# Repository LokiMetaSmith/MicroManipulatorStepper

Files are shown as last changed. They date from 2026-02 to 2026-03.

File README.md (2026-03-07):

# Open Micro-Manipulator

This project contains an open source low-cost, easy-to-build motorized **XYZ Micro-Manipulator** motion control platform achieving submicron precision.
It's designed for applications such as optical alignment, probing electronic components, and microscopy.

Check out the YouTube video for more information about the device and how it is built:<br>
[An Open Source Motorized XYZ Micro-Manipulator - Affordable sub µm Motion Control](https://youtu.be/MgQbPdiuUTw)

<div style="display: flex; gap: 2%;">
  
  
</div>

Thanks to its parallel kinematic structure and miniature ball joints, it achieves good mechanical stiffness and a large range of motion.
The motors are off the shelf stepper motors driven by a 30 kHz closed loop controller and a very precise PWM signal.
A 'magnetic gearing' approach increases the resolution of the low-cost magnetic rotary encoders by a factor of 30 allowing for steps down to 50nm
(**Please mind the difference between resolution and accuracy**. The absolute accuracy is significantly worse.

The device can be controlled via simple G-Code commands over a USB serial interface and is thus easily integrated into other projects.
The firmware implements a complete motion planning stack with look-ahead for smooth and accurate path following capabilities.

## Getting Started

Below is a list of high level steps you can follow if you want to replicate the project. 
If you have questions or problems with the build or just want to discuss subjects related to the project, 
joint the projects community [Discord Server](https://discord.gg/maRvMVpa2Q).

1. Read this Document and watch the linked videos
2. Get the parts listed in [Bill of Materials](documentation/bom/bom.md)
3. Build the device and electronics
4. Change the hardware configuration according to your build [hw_config.h](firmware/MotionControllerRP/src/hw_config.h)
5. Upload firmware using VSCode with PlattformIO plugin
6. Calibrate axis

## ✨NEW: Hardware Version 4.0
A new version of the hardware has been released, fixing several issues with the previous design:

- Self collision during homing fixed.
- Connection of ball joint block with screws only was not well constrained and could rotated a bit.
- No reliable way to ensure consistent linkage rod length
- Unnecessary ball joint friction
- Accurate ball position heavily dependet on print quality and corner rounding
- Rubber bands could not be changed or removed once glued in.

A video about the improved ball joint and linkage manufactoring process can be found on YT: [Better Ball Joints for the Open Micro-Manipulator](https://www.youtube.com/watch?v=NM2KXvRGmpg)
Also the FreeCAD model was restructured and improved and now includes all pins and fasteners. It now provides a reference for all required mechanical parts. 

WARNING: BOM is not updated yet...

## Open Micro-Manipulator GUI
To make testing and using the Open-Micro Manipulator easy and convenient a python control program with a graphical user interface is provided here: [Open Micro-Manipulator GUI](https://github.com/0x23/OpenMicroManipulatorGUI).
It has simple controlls to move the device around, while also displaying a live camera feed (e.g. from a microscope camera). Additional features, include a simple g-code runner and realtime mouse control (e.g. for Biology applications).

<div style="display: flex;">
    Open Micro-Manipulator GUI
</div>

## 🐍 Python-API

The lightweight Python API handles all serial communication and provides convenient command execution and debug message printing.
The interface includes functions to home, move, and calibrate the device, as well as to query device information.
It is structured as a standard Python package for easy installation.

### Installation

You can install the package directly from the repository using pip:

```bash
pip install git+https://github.com/0x23/MicroManipulatorStepper.git#subdirectory=software/PythonAPI
```

Or, if you have cloned the repository locally:

```bash
pip install ./software/PythonAPI
```

## Usage Example
```python
from open_micro_manipulator import OpenMicroStageInterface
from open_micro_manipulator.exceptions import DeviceNotFoundError

# create interface and connect
# Use mock=True for simulation/digital twin
oms = OpenMicroStageInterface(show_communication=True, show_log_messages=True, mock=False)

try:
    oms.connect('/dev/ttyACM0')
except DeviceNotFoundError:
    print("Could not connect to device")

# run this once to calibrate joints
# for i in range(3): oms.calibrate_joint(i, save_result=True)

# home device
oms.home()

# move to several x,y,z positions [mm]
oms.move_to(0.0, 0.0, 0.0, f=10)
oms.move_to(3.1, 4.1, 5.9, f=26)
oms.move_to(0.0001, 0.0, 0.0, f=10)

# wait for moves to finish
oms.wait_for_stop()
```

## API Functions (most relevant functions only)
```python
connect(port, baud_rate=921600)
disconnect()
set_workspace_transform(transform)
get_workspace_transform()
home(axis_list=None)
calibrate_joint(joint_index, save_result)
move_to(x, y, z, f, move_immediately, blocking, timeout)
set_pose(x, y, z)
dwell(time_s, blocking, timeout)
enable_motors(enable)
wait_for_stop(polling_interval_ms, disable_callbacks)
set_max_acceleration(linear_accel, angular_accel)
set_servo_parameter(pos_kp, pos_ki, vel_kp, vel_ki, vel_filter_tc)
```

## ✨ Firmware v1.0.1

This update improves calibration, homing, logging, and adds several new G-Code commands.

### Improvements
- **Homing**: parallel homing support, higher repeatability, more accurate geometric reference  
- **Joint calibration**: refined procedure, persistent flash storage (no recalibration after reboot)  
- **Logging**: clearer and more detailed output  

### New G-Code Commands
- `G28` — Home joints (supports homing multiple axis simultanously for faster startup)
- `G24` — Set pose command (directly sets servo targets, bypassing motion controller)  
- `M17/M18` — Enable/Disable motors (with pose recovery from encoders on enable)  
- `M51` — Read encoder values  
- `M55` — Set servo loop parameters 
- `M56` — Joint calibration (with save-to-flash option)  
- `M57` — Read various information about the device state  
- `M58` — Read firmware version

## ⚙ CAD-Files

All CAD models are made in **FreeCAD** to allow everyone to view and modify the design without subscribing or paying for a proprietary CAD solution.
Note that most components are already designed with the goal to make them easily machinable on a 3-Axis CNC-Mill.
You can also 3D-Print the parts but have to live with thermal drift (carbon filled filaments can reduce this problem).

<div style="display: flex;">
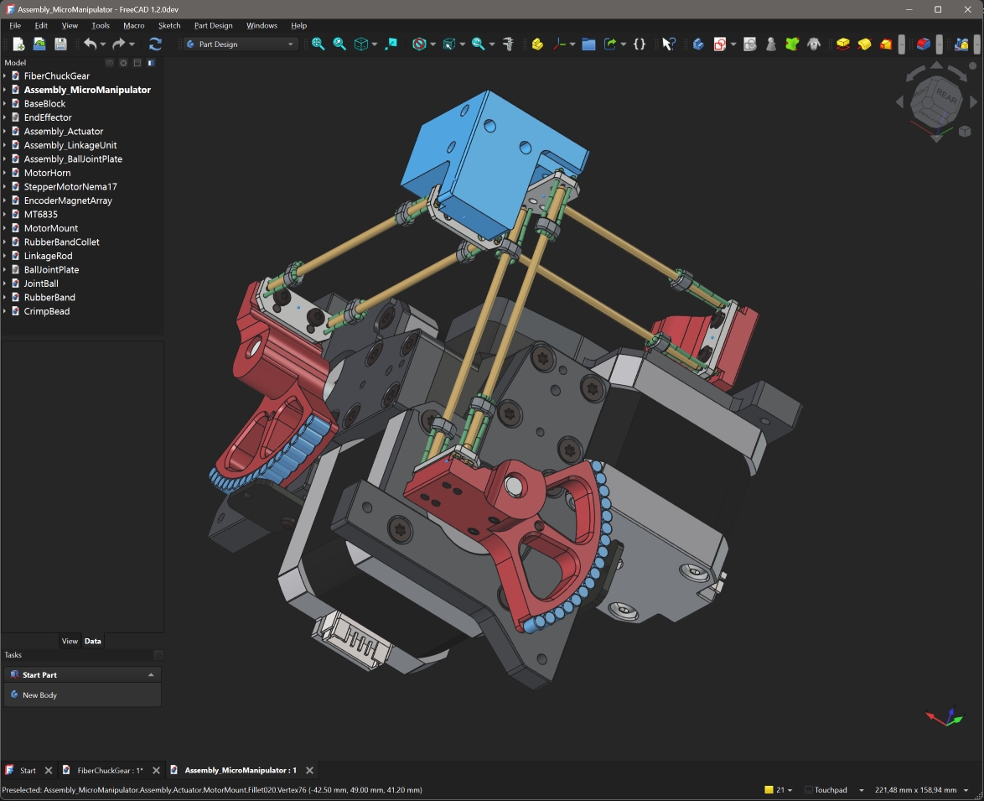
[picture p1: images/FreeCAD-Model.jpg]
FreeCAD Model
    
</div>

<br>

The CAD files can be found here: [CAD Models](construction).
Please note that FreeCAD version **1.2.0dev** was used, and the files might not work with older versions.

STL files for printing can be found here: [STL Files](construction/STL_3D_Printing/)

## ⚙ Testing & Simulation

This project now includes Python scripts for unit testing CAD models, verifying kinematics, and setting up FEA simulations.
See [tests/freecad_scripts/README.md](tests/freecad_scripts/README.md) for details.

To run tests (requires FreeCAD):
```bash
freecadcmd tests/freecad_scripts/run_all_tests.py
```

## ⚙ Kinematic Model

The kinematic model is defined here: [kinematic_model_delta3d.cpp](firmware/MotionControllerRP/src/kinemtaic_models/kinematic_model_delta3d.cpp).
Please check the dimensions of your build against the values set in the constructor. In particular, make sure the arm length matches.

## ⚙ Electronics

IMPORTANT: If you fabricated PCB version v1.2 (see version label on the board) you need to drill out a misplaced via on diode D1 that shorts 5V rail to ground (See [repair image](electronics/pcb_v1.2_fix.jpg) ). The problem was fixed in v1.3.

The electronics are designed in **KiCAD** and only commonly available modules (motor drivers and MCU boards) are used and connected by a simple PCB. No SMD soldering is required to populate the board to make the build extra accessible.
For usual winding resistance of your motors, the device should be powered by $${\color{lightgreen} 5V-6V }$$ (2A) to keep current and heating to a reasonable level.

<div style="display: flex; gap: 5%;">
  
  
</div>

The repository now also contains the fabrication files that can be directly uploaded to the PCB manufacturer.

## ⚙ Firmware

The firmware is written in C++ and takes some inspiration from the 'SimpleFOC' project. It aims to be streamlined and readable without any extra fuss, focusing on the hardware used in this project.
It implements path planning with look-ahead and, unlike many other motion controller projects, supports true 6DOF-Pose interpolation and planning, making it ready for driving hexapod motion platforms; that may or may not be the next step for this project.

You may find configuration for pin numbers, motor type, and other parameters in [hw_config.h](firmware/MotionControllerRP/src/hw_config.h). Please check them before uploading the firmware.

<div style="display: flex; gap: 2%;">
  
  
</div>

### Building and Flashing the Firmware

For building and flashing the firmware, Visual Studio Code (available for free on Windows and Linux) is recommended.
Install the PlatformIO add-on and open the firmware folder. You can now build and flash the firmware like any other PlatformIO project.

## ⚙ G-Code Interface

The firmware supports only a small subset of G-Code commands listed below.  
Each command is acknowledged with either an **`ok`** or **`error`** response.  

If a command provides additional information (e.g., the *get position* command), that information is returned **before** the `ok` message.  
The client must wait for an acknowledgment from the previous command before sending the next one—otherwise, behavior is undefined.
| Command           | Description                                                                 |
|-------------------|-----------------------------------------------------------------------------|
| `G0 X Y Z F`   | Move the end-effector in a straight line to the specified position. <br>• `X`, `Y`, `Z`: target positions <br>• `F`: feed rate |
| `G1 X Y Z F`   | Same as `G0`.                                                              |
| `G4 S/P`       | Dwell/pause for a specified time. <br>• `S`: seconds <br>• `P`: milliseconds |
| `G24 X Y Z A B C` | Directly set current pose for servo loops with optional rotation vector* `A`, `B`, `C`. |
| `G28 A-F`      | Home one or more joints. <br>• Optional joint selection `A`–`F`.           |
| `M17`          | Enable motors and read current pose as the start pose.                     |
| `M18`          | Disable motors.                                                            |
| `M50`          | Get current internal pose. (Encoders are not read here)                                   |
| `M51`          | Get current encoder angles (in degrees) and raw encoder values.              |
| `M52`          | Get the number of items in the planner queue.                               |
| `M53`          | Check if all planned moves are finished (`1` = finished, `0` = not finished). |
| `M55 A B C D F` | Set servo loop parameters. <br>• `A`, `B`: position PI controller gains (P and I) <br>• `C`, `D`: velocity PI controller gains (P and I) <br>• `F`: velocity filter time constant |
| `M56 J S`      | Calibrate a joint. <br>• `J`: joint index <br>• `S`: save calibration result |
| `M57`          | Get device and servo loop info: homing/calibration state, angles, loop frequencies, and file list. |
| `M58`          | Get firmware version.                                                      |
| `M204 L A`     | Set linear and angular acceleration. <br>• `L`: linear acceleration <br>• `A`: angular acceleration |

*Note: The communication protocol uses 3D vectors for rotations. The direction represents the rotation axis and the length of the vector represents the angle of rotation around the axis.

## ❤️ Support

If you'd like to support this project, consider the following:

- **Contribute to the build guide** – Help improve or expand the build instructions by submitting pull requests or opening issues with suggestions.
- **Characterize typical radial stepper motor shaft error motion** – Measure radial error motion of the shaft of multiple Nema-17 stepper motors (see Cylos Garage for more information about the subject: https://www.youtube.com/watch?v=gt2gK-oxy5s).
- **Give feedback on the build experience** – Let us know what worked, what didn’t, and how the process could be smoother for others.
- **Support the project on Ko-fi** – If you find this project valuable, you can support it financially via [Ko-fi](https://ko-fi.com/diffractionlimited) ☕.

## Youtube Video
Watch the video (https://youtu.be/MgQbPdiuUTw)

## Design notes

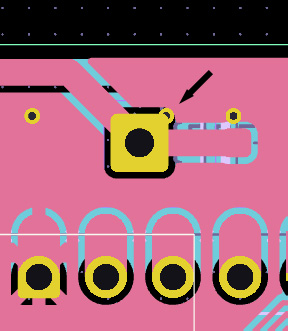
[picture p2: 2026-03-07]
electronics/control_board/pcb_v1.2_fix.jpg

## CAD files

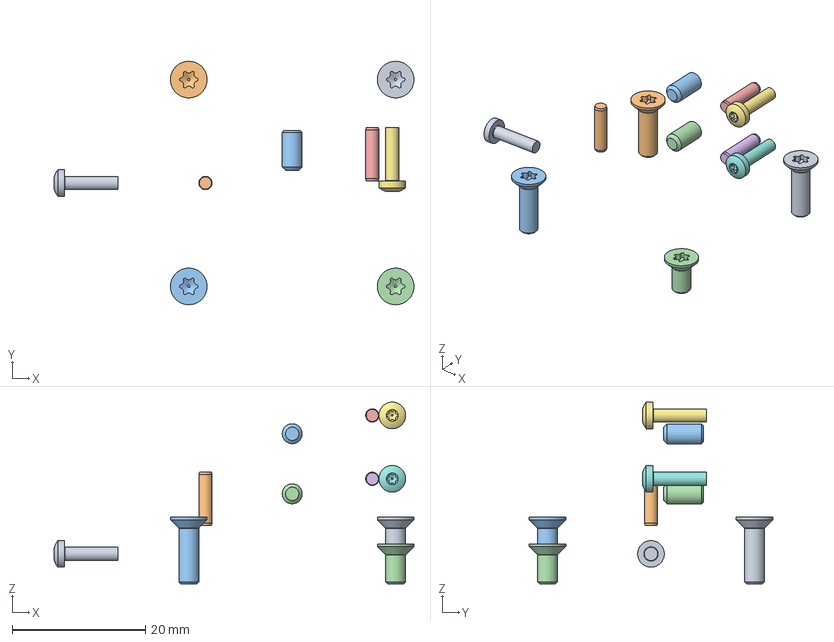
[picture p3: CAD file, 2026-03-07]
construction/micro_manipulator/Assembly_Actuator.FCStd
53.9 x 36.5 x 27.2 mm
M3x10-Screw x 2
M3x10-Screw008 x 2
M3x10-Screw009 x 2
M3x6-Screw x 2
2 mmx8-Pin x 2
2 mmx8-Pin012 x 2
M2x8-Screw x 2
M2x8-Screw009 x 2
M2x8-Screw004 x 2
2 mmx8-Pin011 x 2
M3x6-Screw003 x 2
M3x6-Screw004 x 2

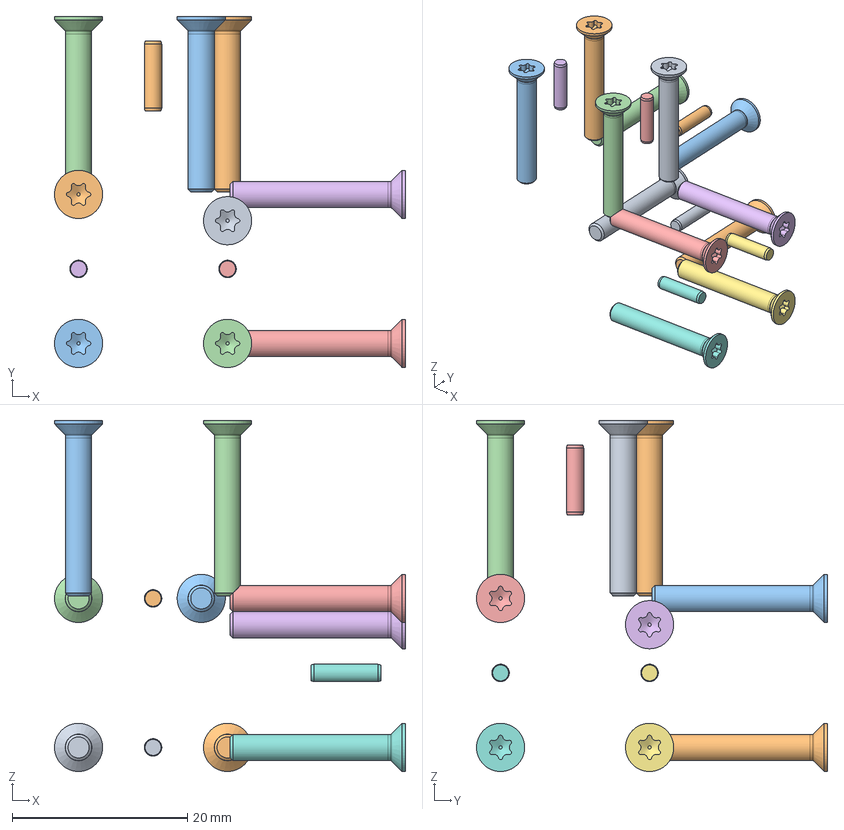
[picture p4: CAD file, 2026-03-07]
construction/micro_manipulator/Assembly_MicroManipulator.FCStd
40.0 x 40.0 x 40.0 mm
M3x20-Screw x 2
M3x20-Screw281 x 2
M3x20-Screw282 x 2
M3x20-Screw283 x 2
M3x20-Screw277 x 2
M3x20-Screw278 x 2
M3x20-Screw279 x 2
M3x20-Screw280 x 2
M3x20-Screw262 x 2
M3x20-Screw263 x 2
M3x20-Screw264 x 2
M3x20-Screw265 x 2
2 mmx8-Pin027 x 2
2 mmx8-Pin028 x 2
2 mmx8-Pin029 x 2
2 mmx8-Pin030 x 2
2 mmx8-Pin031 x 2
2 mmx8-Pin032 x 2

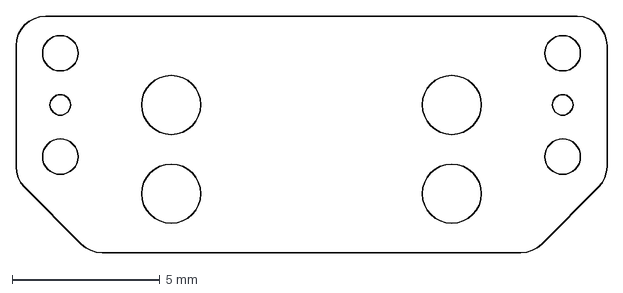
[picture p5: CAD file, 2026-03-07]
construction/micro_manipulator/balljoint_plate_pcb/BallJointPlate-Contour.dxf
20.0 x 8.00 mm

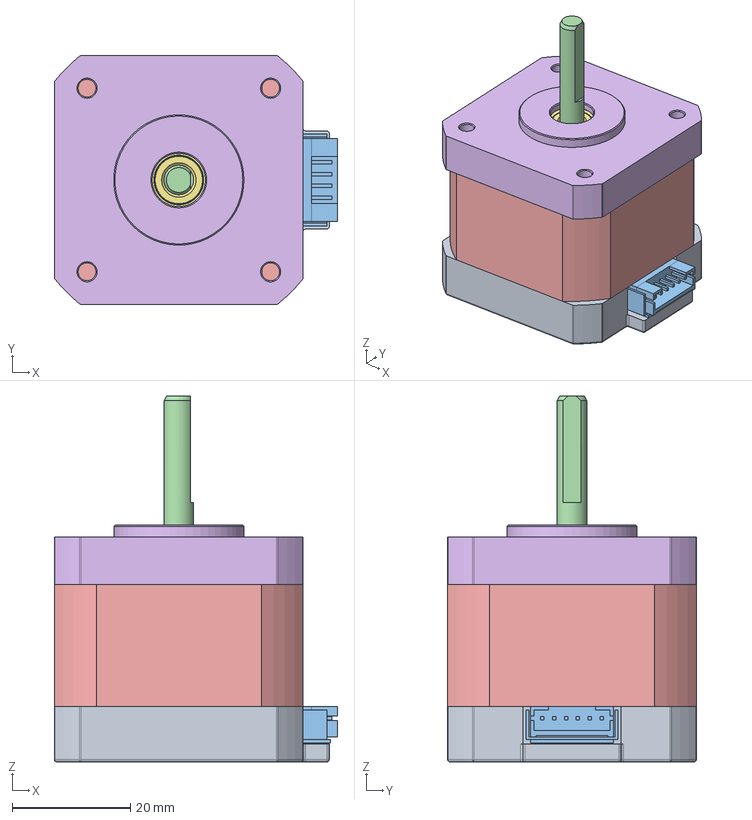
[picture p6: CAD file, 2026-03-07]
construction/micro_manipulator/StepperMotorNema17.FCStd
47.8 x 42.0 x 61.8 mm
rear end cap
rear bearing
connector
shaft
stator
front end cap
front bearing
M3x10-Screw
M3x10-Screw004
M3x10-Screw005
M3x10-Screw006

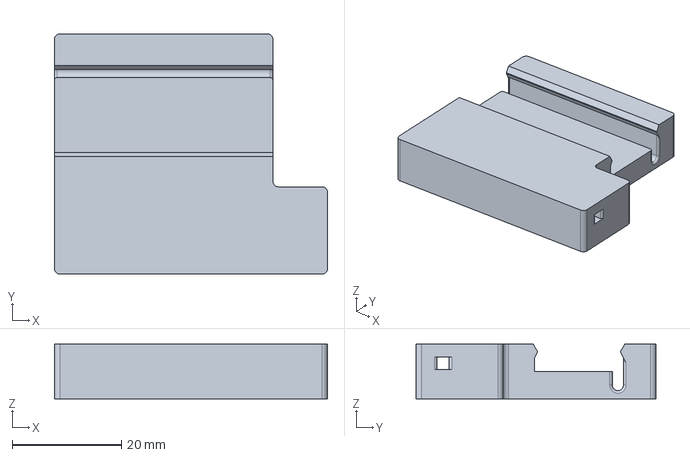
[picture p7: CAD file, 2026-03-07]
construction/tools/rod_embossing_tools/rod_lenth_setting_press/rod_guide.FCStd
50.0 x 44.0 x 10.0 mm

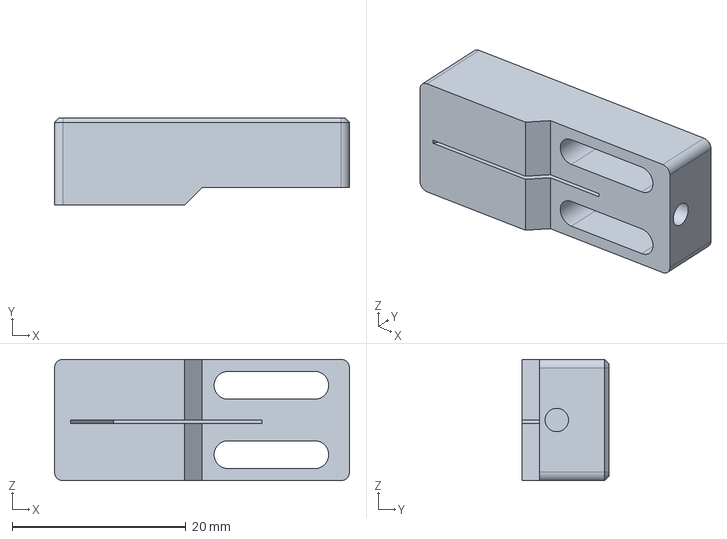
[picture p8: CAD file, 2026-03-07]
construction/tools/rod_embossing_tools/rod_sharper/BladeCarrier.FCStd
34.0 x 10.0 x 14.0 mm

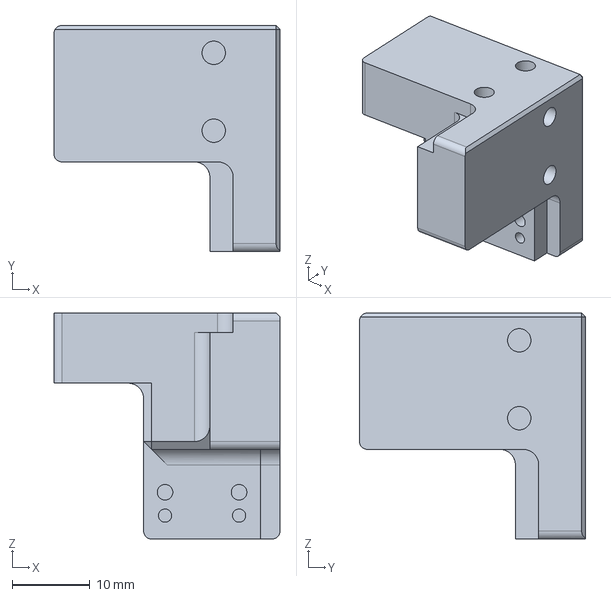
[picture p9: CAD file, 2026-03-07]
construction/micro_manipulator/EndEffector.FCStd
29.0 x 29.0 x 29.0 mm

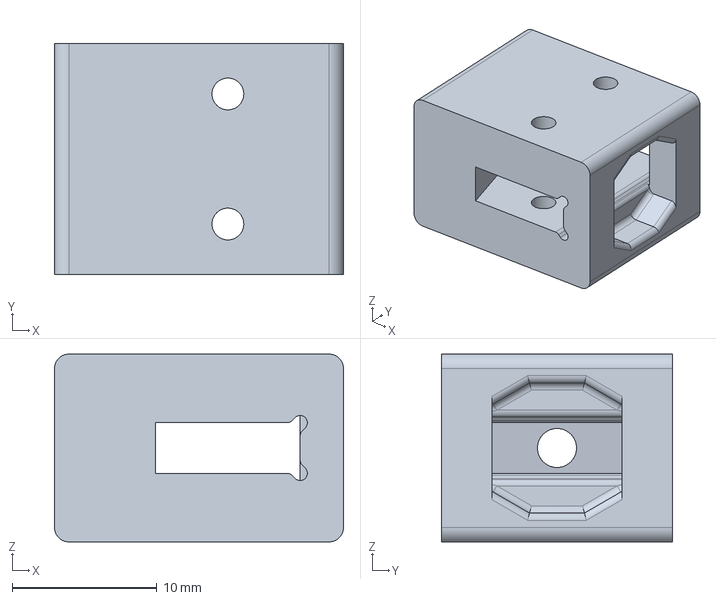
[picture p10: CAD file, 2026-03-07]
construction/tools/rod_embossing_tools/rod_lenth_setting_press/caliper_clamp.FCStd
20.0 x 16.0 x 13.0 mm

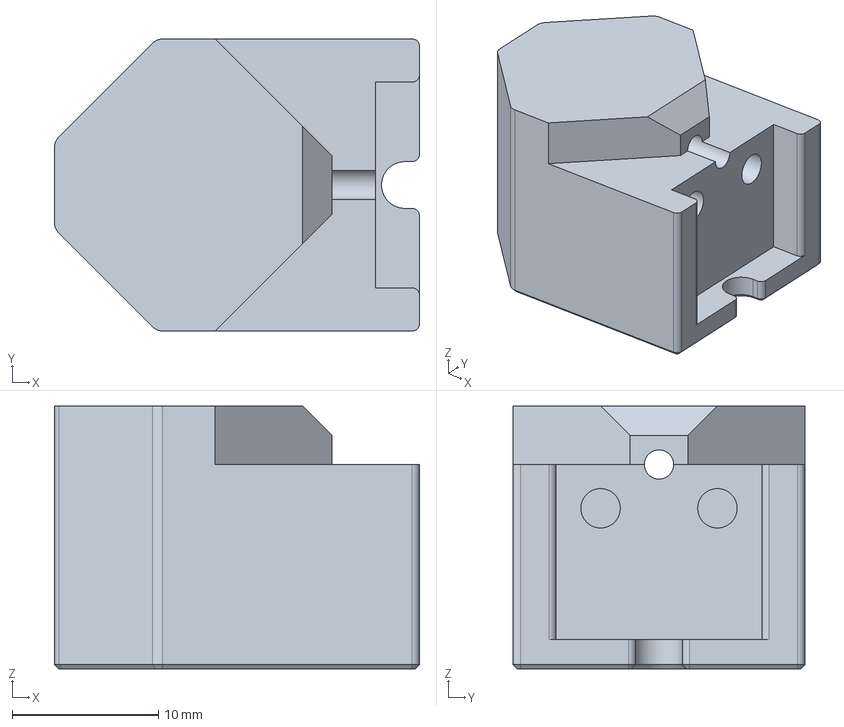
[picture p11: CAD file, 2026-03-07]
construction/tools/rod_embossing_tools/rod_sharper/RodGuide.FCStd
25.0 x 20.0 x 18.0 mm

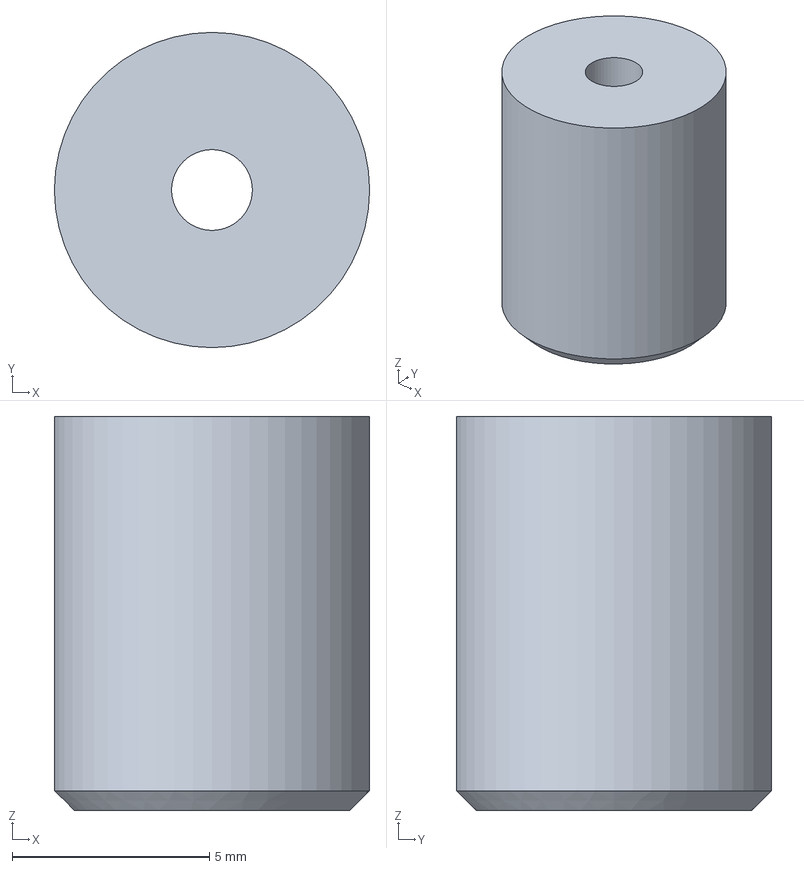
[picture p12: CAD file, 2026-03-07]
construction/tools/rod_embossing_tools/rod_lenth_setting_press/rod_collet.FCStd
8.00 x 8.00 x 10.0 mm

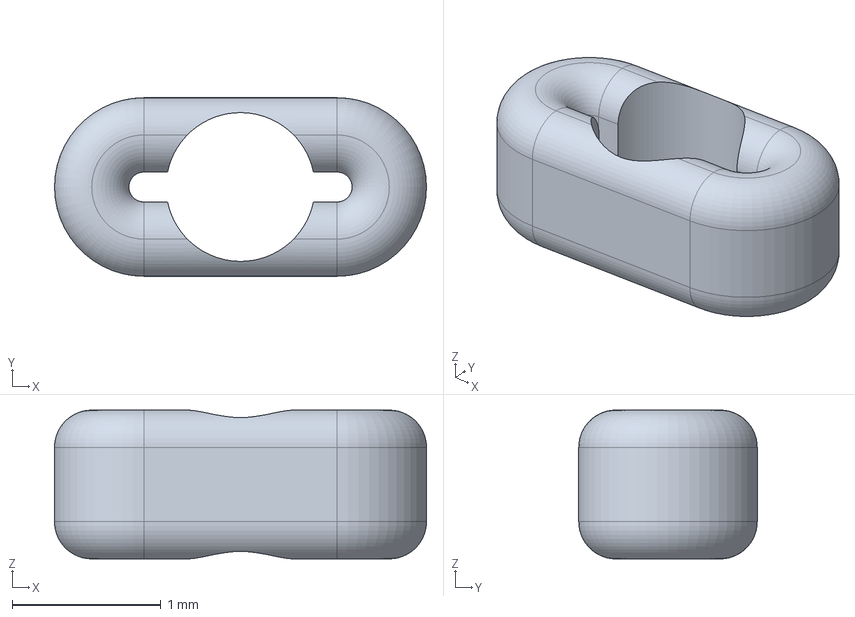
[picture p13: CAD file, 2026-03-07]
construction/micro_manipulator/CrimpBead.FCStd
2.50 x 1.20 x 1.00 mm

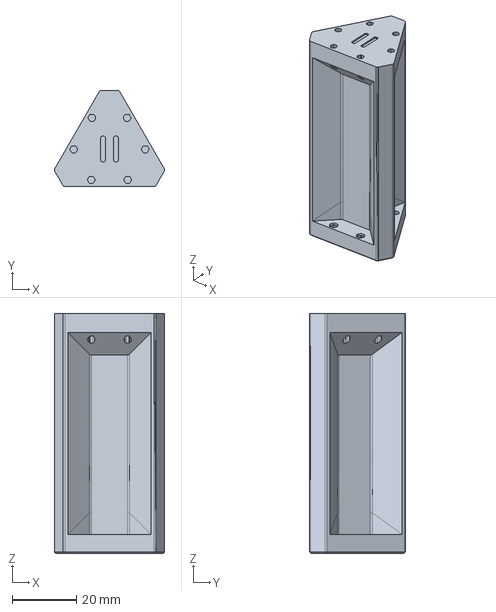
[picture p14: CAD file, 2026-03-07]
construction/tools/rod_embossing_tools/rod_lenth_setting_press/RodGrindingJig_B.FCStd
34.5 x 30.1 x 75.0 mm

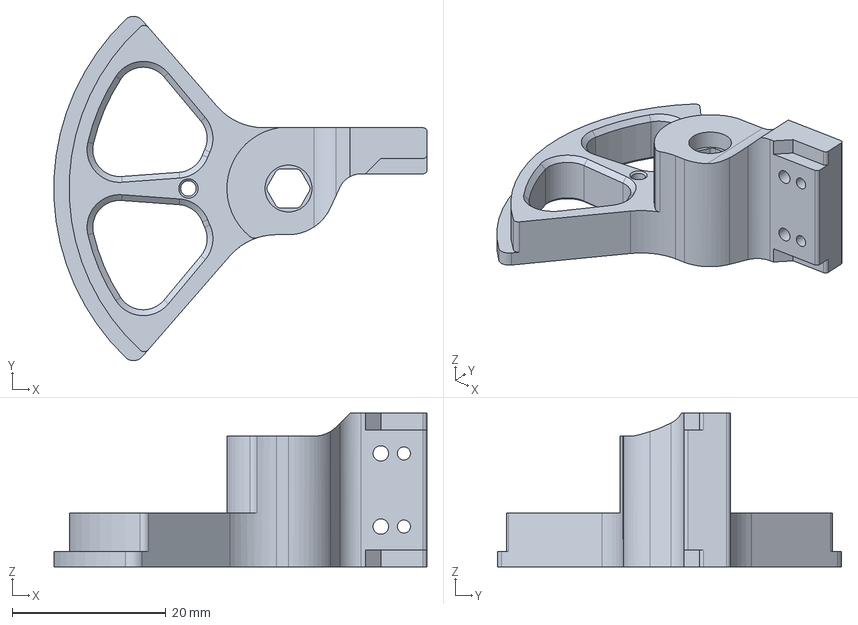
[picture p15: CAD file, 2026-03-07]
construction/micro_manipulator/MotorHorn.FCStd
48.5 x 44.7 x 20.0 mm

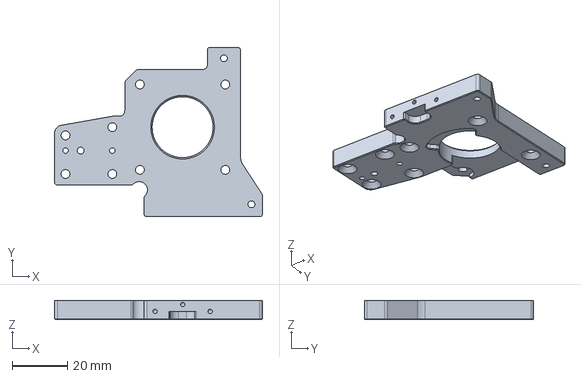
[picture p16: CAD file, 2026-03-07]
construction/micro_manipulator/MotorMount.FCStd
75.5 x 61.5 x 7.00 mm

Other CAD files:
construction/micro_manipulator/Assembly_EndEffector.FCStd
construction/micro_manipulator/Assembly_BallJointPlate.FCStd
construction/micro_manipulator/Assembly_LinkageUnit.FCStd
construction/tools/rod_embossing_tools/rod_lenth_setting_press/RodGrindingJig_A.FCStd
construction/micro_manipulator/BallJointPlate.FCStd
construction/micro_manipulator/BaseBlock.FCStd
construction/micro_manipulator/EncoderMagnet.FCStd
construction/micro_manipulator/EncoderMagnetArray.FCStd
construction/micro_manipulator/JointBall.FCStd
construction/micro_manipulator/LinkageRod.FCStd
construction/micro_manipulator/MT6835.FCStd
construction/micro_manipulator/RubberBand.FCStd
construction/micro_manipulator/RubberBandCollet.FCStd

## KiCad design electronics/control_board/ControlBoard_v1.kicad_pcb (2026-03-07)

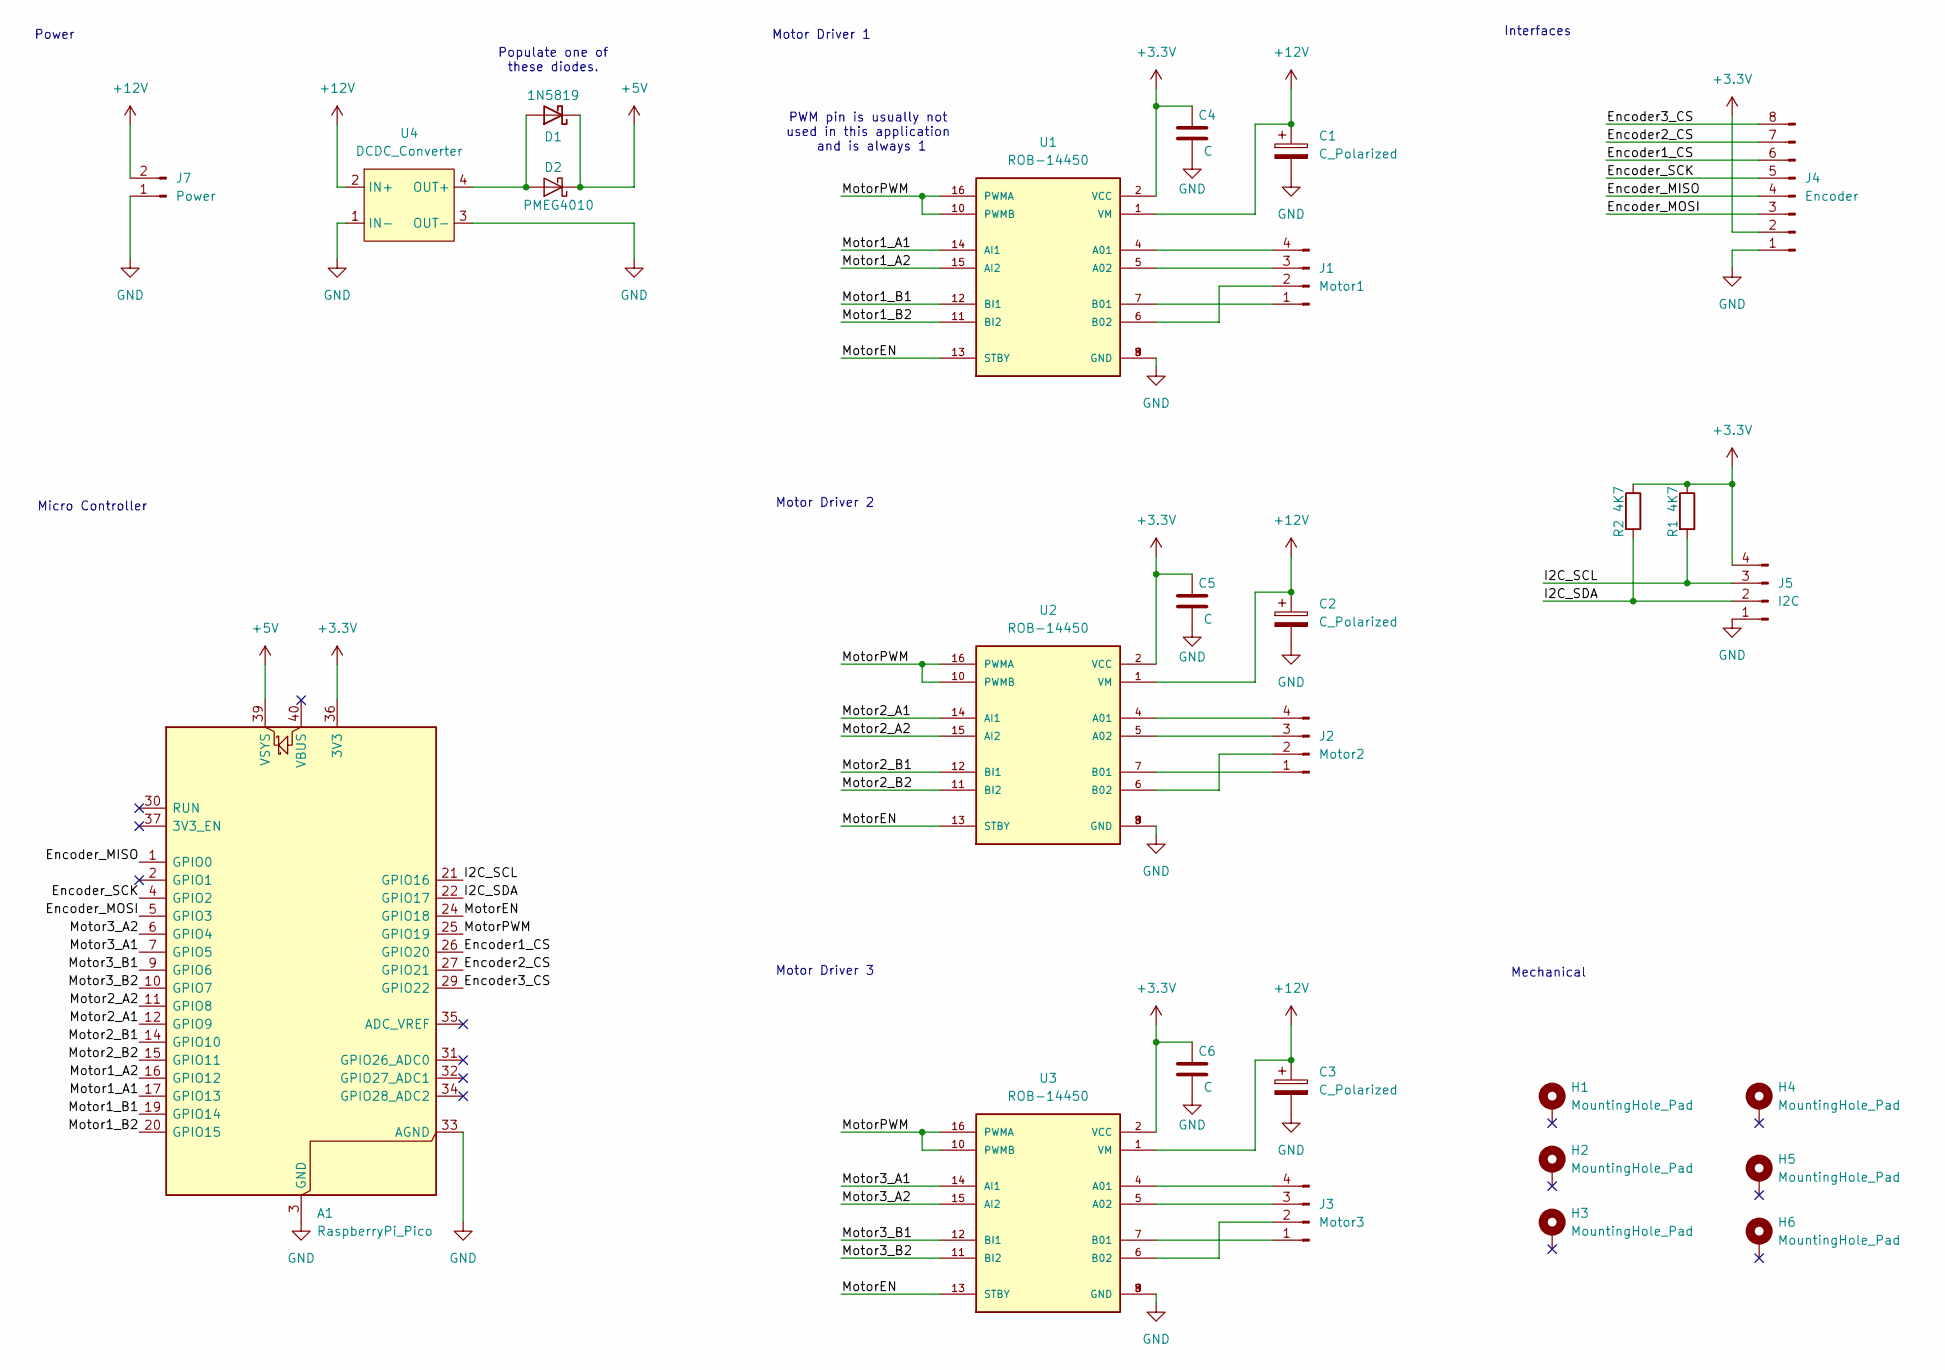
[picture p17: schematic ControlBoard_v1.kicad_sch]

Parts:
A1: RaspberryPi_Pico; RaspberryPi_Pico_Common_Unspecified
C1, C2, C3: C_Polarized; CP_Radial_D8.0mm_P3.50mm
C4, C5, C6: C; C_0603_1608Metric_Pad1.08x0.95mm_HandSolder
D1: 1N5819; D_DO-41_SOD81_P10.16mm_Horizontal
D2: PMEG4010; D_SOD-123F
H1, H2, H3, H4, H5, H6: MountingHole_Pad; MountingHole_2.7mm_M2.5_Pad_Via
J1: Motor1; PinHeader_1x04_P2.54mm_Vertical
J2: Motor2; PinHeader_1x04_P2.54mm_Vertical
J3: Motor3; PinHeader_1x04_P2.54mm_Vertical
J4: Encoder; JST_PH_B8B-PH-K_1x08_P2.00mm_Vertical
J5: I2C; JST_PH_B4B-PH-K_1x04_P2.00mm_Vertical
J7: Power; AMASS_XT60-M_1x02_P7.20mm_Vertical
R1, R2: 4K7; R_0603_1608Metric_Pad0.98x0.95mm_HandSolder
U1, U2, U3: ROB-14450; MODULE_ROB-14450; PARTREV 11-13-17
U4: DCDC_Converter; DCDC_17mmx12mm

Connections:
+3.3V: A1.36 (3V3), C4.1, C5.1, C6.1, J4.2, J5.4, R1.1, R2.1, U1.2 (VCC), U2.2 (VCC), U3.2 (VCC)
+5V: A1.39 (VSYS), D1.1 (K), D2.1 (K)
+12V: C1.1, C2.1, C3.1, J7.2, U1.1 (VM), U2.1 (VM), U3.1 (VM), U4.2 (IN+)
/Encoder1_CS: A1.26 (GPIO20), J4.6
/Encoder2_CS: A1.27 (GPIO21), J4.7
/Encoder3_CS: A1.29 (GPIO22), J4.8
/Encoder_MISO: A1.1 (GPIO0), J4.4
/Encoder_MOSI: A1.5 (GPIO3), J4.3
/Encoder_SCK: A1.4 (GPIO2), J4.5
/I2C_SCL: A1.21 (GPIO16), J5.3, R1.2
/I2C_SDA: A1.22 (GPIO17), J5.2, R2.2
/Motor1_A1: A1.17 (GPIO13), U1.14 (AI1)
/Motor1_A2: A1.16 (GPIO12), U1.15 (AI2)
/Motor1_B1: A1.19 (GPIO14), U1.12 (BI1)
/Motor1_B2: A1.20 (GPIO15), U1.11 (BI2)
/Motor2_A1: A1.12 (GPIO9), U2.14 (AI1)
/Motor2_A2: A1.11 (GPIO8), U2.15 (AI2)
/Motor2_B1: A1.14 (GPIO10), U2.12 (BI1)
/Motor2_B2: A1.15 (GPIO11), U2.11 (BI2)
/Motor3_A1: A1.7 (GPIO5), U3.14 (AI1)
/Motor3_A2: A1.6 (GPIO4), U3.15 (AI2)
/Motor3_B1: A1.9 (GPIO6), U3.12 (BI1)
/Motor3_B2: A1.10 (GPIO7), U3.11 (BI2)
/MotorEN: A1.24 (GPIO18), U1.13 (STBY), U2.13 (STBY), U3.13 (STBY)
/MotorPWM: A1.25 (GPIO19), U1.10 (PWMB), U1.16 (PWMA), U2.10 (PWMB), U2.16 (PWMA), U3.10 (PWMB), U3.16 (PWMA)
GND: A1.3 (GND), A1.8 (GND), A1.13 (GND), A1.18 (GND), A1.23 (GND), A1.28 (GND), A1.33 (AGND), A1.38 (GND), C1.2, C2.2, C3.2, C4.2, C5.2, C6.2, J4.1, J5.1, J7.1, U1.3 (GND), U1.8 (GND), U1.9 (GND), U2.3 (GND), U2.8 (GND), U2.9 (GND), U3.3 (GND), U3.8 (GND), U3.9 (GND), U4.1 (IN-), U4.3 (OUT-)
unnamed: D1.2 (A), D2.2 (A), U4.4 (OUT+)
unnamed: J1.1, U1.7 (B01)
unnamed: J1.2, U1.6 (B02)
unnamed: J1.3, U1.5 (A02)
unnamed: J1.4, U1.4 (A01)
unnamed: J2.1, U2.7 (B01)
unnamed: J2.2, U2.6 (B02)
unnamed: J2.3, U2.5 (A02)
unnamed: J2.4, U2.4 (A01)
unnamed: J3.1, U3.7 (B01)
unnamed: J3.2, U3.6 (B02)
unnamed: J3.3, U3.5 (A02)
unnamed: J3.4, U3.4 (A01)

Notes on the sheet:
PWM pin is usually not used in this application and is always 1
Motor Driver 2
Power
Interfaces
Motor Driver 1
Motor Driver 3
Mechanical
Populate one of these diodes.
Micro Controller

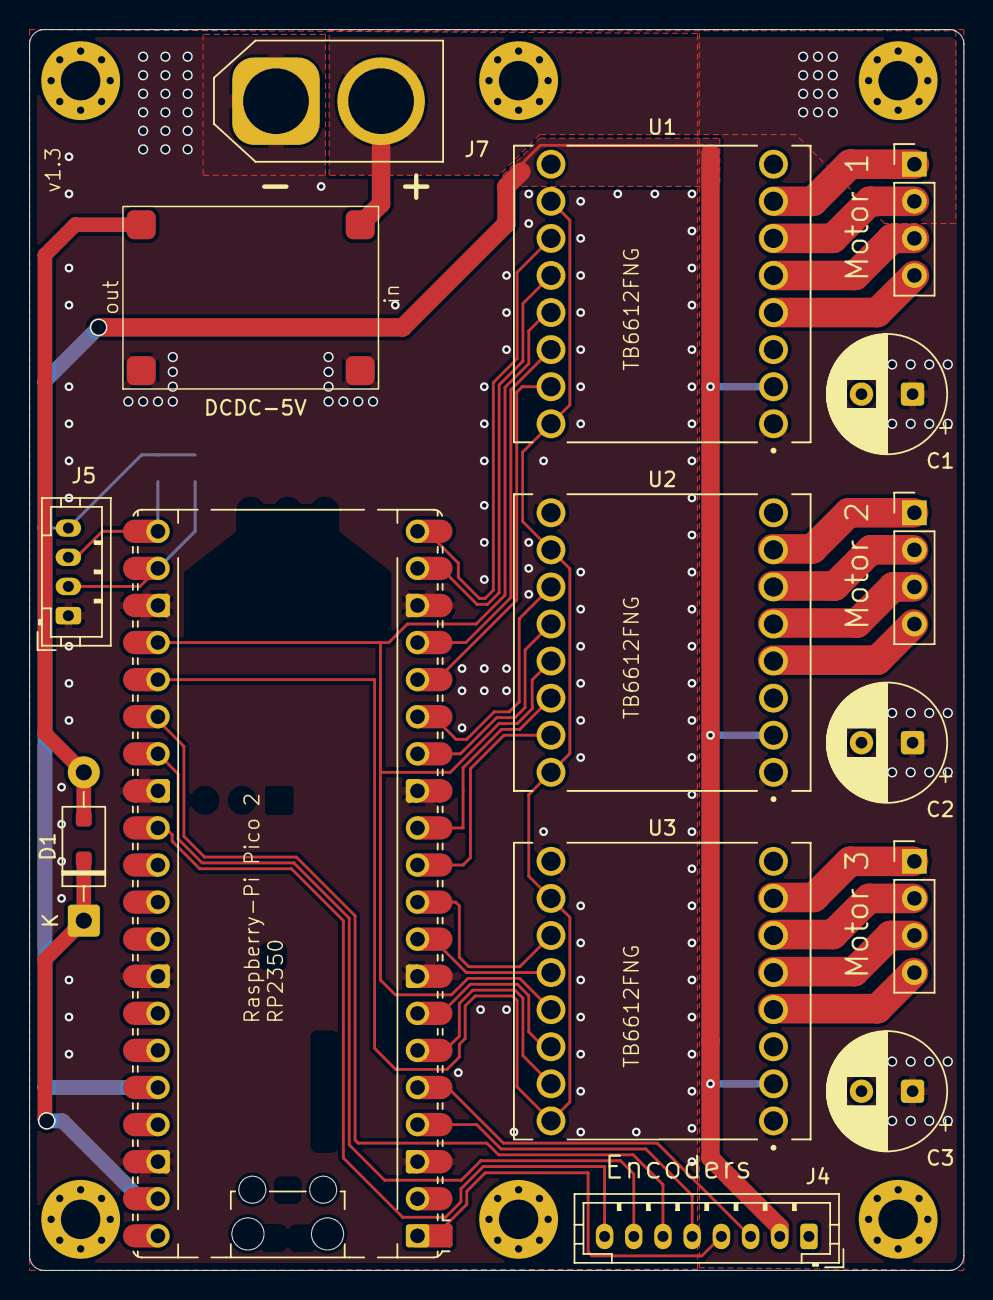
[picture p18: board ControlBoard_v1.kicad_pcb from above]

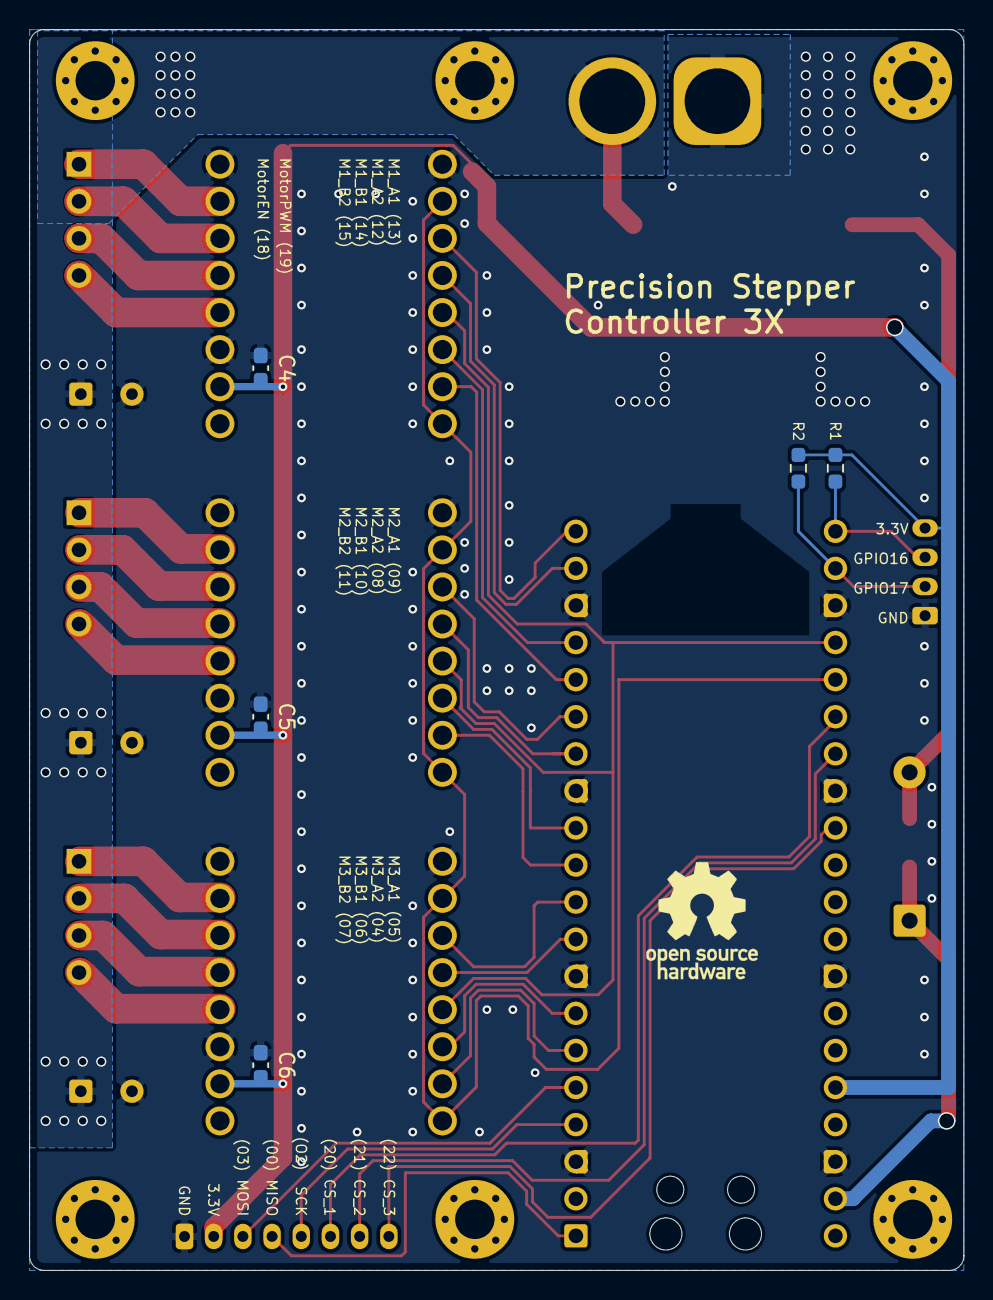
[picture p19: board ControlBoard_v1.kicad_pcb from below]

Board: 2 copper layers, 64.0 x 85.0 mm, 27 parts (6 on the bottom side), 39 nets.

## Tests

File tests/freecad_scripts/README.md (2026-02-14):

# FreeCAD Testing & Simulation

This directory contains Python scripts for testing, verifying, and simulating the FreeCAD models of the Micro-Manipulator project.

## How to Run

These scripts must be run inside the FreeCAD environment, typically via the `freecadcmd` command-line tool.

1.  **Install FreeCAD**: Make sure FreeCAD is installed and in your system path.
2.  **Navigate to Project Root**: `cd MicroManipulatorStepper`
3.  **Run Tests**:
    ```bash
    freecadcmd tests/freecad_scripts/run_all_tests.py
    ```
    This will execute all test cases and report success/failure.

## Scripts

*   `kinematic_model.py`: A Python port of the C++ kinematic model. Used for verifying kinematics against the CAD model.
*   `test_motor_mount.py`: Unit test for the Motor Mount part. Verifies dimensions (Radius).
*   `test_kinematics_validation.py`: Checks if the firmware's kinematic parameters match the CAD dimensions.
*   `setup_fea.py`: Sets up a Finite Element Analysis (FEA) on the motor mount part, applying materials, constraints, and loads.

## Troubleshooting

If you encounter `ModuleNotFoundError: No module named 'FreeCAD'`, ensure you are running the script with `freecadcmd` or `freecad`, NOT standard `python`.

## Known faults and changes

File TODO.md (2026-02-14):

# Open Micro-Manipulator Project TODOs

This file lists potential improvements, features, and bug fixes for the Open Micro-Manipulator project.

## High Priority (Bugs)
- [ ] **Fix `wait_for_stop` busy loop**: The `wait_for_stop` function in `software/PythonAPI/src/open_micro_manipulator/interface.py` polls `M53` in a tight loop without sleeping, causing high CPU usage and potential serial communication flooding.
- [ ] **Fix `home` function axis index check**: The check `if 0 > axis_idx >= len(axis_chars):` is logically incorrect and always evaluates to False. It should be `if axis_idx < 0 or axis_idx >= len(axis_chars):`.

## Features & Improvements
- [x] **Implement `read_encoder_angles`**: The function `read_encoder_angles` in the Python API is currently a stub. It should parse the output of the `M51` command.
- [x] **Implement `read_device_state_info` parsing**: The function `read_device_state_info` sends `M57` but does not parse or return the device state information.
- [ ] **Add Rotation Support to `set_pose`**: The `set_pose` function only supports translation (X, Y, Z). It should be extended to support rotation (A, B, C) as per the firmware capabilities.
- [ ] **Add Context Manager Support**: Implement `__enter__` and `__exit__` methods in `OpenMicroStageInterface` to allow usage with the `with` statement (automatically closing the connection).
- [ ] **Add Type Hinting and Docstrings**: Improve type hinting and docstrings throughout the Python API for better developer experience.
- [ ] **Add Unit Tests**: Expand the test suite to cover more API functions and edge cases, potentially using `pytest`.
- [ ] **Add CLI Tool**: Create a simple command-line interface (CLI) to control the manipulator without writing Python scripts.

## Firmware
- [ ] **Verify `M51` output format**: Ensure the firmware output for `M51` is consistent and easy to parse.
- [ ] **Add detailed error codes**: Improve error reporting in G-Code responses.

## Documentation
- [ ] **Update API Documentation**: Ensure the README or separate API docs reflect the latest changes and features.

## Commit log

2026-02-14 Refactor Python API: packaging, mock interface, error handling, types, calibration result, updated docs
2026-02-14 Implement read_device_state_info and update TODO list
    - Implement parsing of M57 command in `read_device_state_info` to return `DeviceState`.
    - Add `DeviceState` and `JointState` dataclasses in `types.py`.
    - Update `MockSerialInterface` to simulate M57 response.
    - Add unit tests for `read_device_state_info` and `read_encoder_angles` in `software/PythonAPI/tests/test_interface.py`.
    - Update `TODO.md` marking completed tasks.
